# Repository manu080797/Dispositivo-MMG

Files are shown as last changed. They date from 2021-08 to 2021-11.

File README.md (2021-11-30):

# Mecanomiografía: desarrollo de un dispositivo para el monitoreo del límite de fatiga muscular

## Descripción del repositorio

Este es el repositorio del proyecto integrador "Mecanomiografía: desarrollo de un dispositivo para el monitoreo del límite de fatiga muscular" para la carrera de ingeniería mecánica en el <a href="https://www.ib.edu.ar">Instituto Balseiro</a>. En la carpeta <a href="https://github.com/manu080797/Dispositivo-MMG/tree/main/Documentos">Documentos</a> se incluye una <a href="https://github.com/manu080797/Dispositivo-MMG/raw/main/Documentos/Presentación%20final.pptx.zip">presentación de PowerPoint</a> que sirve como introducción al trabajo realizado. Además, se incluye la <a href="https://github.com/manu080797/Dispositivo-MMG/raw/main/Documentos/Mecanomiograf%C3%ADa%20desarrollo%20de%20un%20dispositivo%20para%20el%20monitoreo%20del%20l%C3%ADmite%20de%20fatiga%20muscular.pdf">tesis completa</a> en formato PDF. En la carpeta <a href="https://github.com/manu080797/Dispositivo-MMG/tree/main/Programas">Programas</a> se encuentra el código de los tres programas desarrollados durante el proyecto.  En la carpeta <a href="https://github.com/manu080797/Dispositivo-MMG/tree/main/Electrónica">Electrónica</a> están los archivos de <a href="https://www.kicad.org">KiCAD</a> utilizados para diseñar y construir los circuitos electrónicos del dispositivo. Por último, en la carpeta <a href="https://github.com/manu080797/Dispositivo-MMG/tree/main/Carcasa">Carcasa</a> se incluyen archivos de <a href="https://solidedge.siemens.com/en/solutions/products/complete-product-development-portfolio/whats-new-in-solid-edge-2021/">SolidEdge 2021</a> con el modelo 3D de la carcasa del dispositivo, la cual fue construida con una impresora 3D.

## Resumen
En esta tesis se desarrolló un dispositivo de adquisición de señal para mecanomiografía de bajo costo, replicable y portátil. El mismo consta de un acelerómetro, electrónica de acondicionamiento de señal y una placa de desarrollo en la que se adquieren las señales de dos canales en simultáneo. Estas se procesan digitalmente y son transmitidas de manera inalámbrica a una aplicación multiplataforma de control y comunicación también desarrollada en este trabajo. Esta aplicación permite visualizar las señales en tiempo real y almacenar capturas. Estas se procesan fuera de línea según una metodología también diseñada en este trabajo para determinar qué parámetros de la señal se relacionan con la actividad muscular. Los parámetros se calcularon sobre la señal original, sobre bandas de frecuencia específicas y sobre la distribución espectral de potencia. Por último, se realizaron experimentos para aplicar la metodología propuesta a las señales adquiridas por el dispositivo desarrollado. Se realizaron ejercicios isométricos de extensión de rodilla sobre un brazo de reacción fijo vinculado a una celda de carga. Se midió la señal de mecanomiografía sobre el recto femoral de 5 sujetos en ejercicios a carga máxima, a distintos porcentajes de la carga máxima, y hasta el fallo de la tarea solicitada; y se realizaron pruebas de impacto sobre el músculo para evaluar las propiedades mecánicas del mismo. Se procesaron 145 parámetros, de los cuales se encontraron 12 con alta correlación con la fuerza ejercida (coeficiente de correlación r de Pearson ≥ 0,8). Con las pruebas de impacto se encontró que la frecuencia natural del músculo aumenta con la fuerza. En ejercicios al fallo de la tarea solicitada, se encontró que los 12 parámetros seleccionados mantienen el valor esperado con la correlación hallada, para la carga del ejercicio, durante al menos 10 segundos, y luego presentan desviaciones significativas, pero con sentidos variados entre sujetos. Los parámetros relacionados con la energía de la señal en la banda de 50 a 75 Hz presentaron una correlación superior al resto (r = 0,9) y desviaciones con el tiempo en los ejercicios al fallo consistentes en todos los sujetos y cargas evaluadas.

### Descripción del dispositivo


### Arquitectura del dispositivo


### Arreglo experimental



### Señal cruda en ejercicio al fallo de la tarea solicitada


### Procesamiento de señal
 

### 1) Señal cruda 2) Subbanda de frecuencia 3) Parámetro


## Abstract
A low cost, replicable and portable signal acquisition device for mechanomiography was developed in this thesis. It comprises an accelerometer, its signal conditioning electronics and a development board that acquires the signal in two channels. The signal is digitally processed and wirelessly transmitted to a multi-platform control and communication App, which is also developed in this thesis. This App enables the realtime visualization of the signal and its storage for offline processing, using a methodology designed in this thesis to get correlated features with muscle activity. These features where computed over the original signal, some band filtered components and the power spectrum density. Finally, experiments where conducted to apply the developed methodology to the signal acquired by the device. These experiments consisted of isometric knee extension exercises against a fixed reaction arm linked to a load cell. The mechanomiogram signal was acquired from the rectus femoris muscle of 5 participants at maximum load, at intermediate loads, and to task failure. Additionally, bump tests where conducted to evaluate the muscle mechanical properties. 145 features where processed, of which only 12 showed a high correlation with force (Pearson’s r correlation coefficient ≥ 0,8). Muscle natural frequency was found to increase with higher force production. The 12 selected parameters presented a constant value during the first 10 seconds of a fatiguing exercise, but showed significant deviations from the expected value after this, with varying directions between subjects. From the selected features, those related with the signal energy at the 50-75 Hz band presented both the highest correlation (r = 0,9) and the most consistent deviations sense, in task failure exercises among all subjects and loads.

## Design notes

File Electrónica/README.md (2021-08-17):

# Electrónica

Diagramas esquemáticos y PCB de los circuitos desarrollados. Los mismos se desarrollaron utilizando el software KiCad v5.0.1.

manufactura_pcb

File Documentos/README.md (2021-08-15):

# Documentos

Para una introducción rápida de la tesis ver a presentación de powerpoint. Se debe visualizar con Microsoft PowerPoint en modo presentación, ya que incluye videos y animaciones. En caso de mayores detalles se puede consultar la tesis completa en el archivo PDF.

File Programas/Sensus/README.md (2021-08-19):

# Sensus
Firmware para Sensus (basado en placa de desarrollo Espressif ESP32)

### Flujo de procesamiento de datos


### Diagrama de clases
diagrama_clases_firmware

### Diagrama GRAFCET de la gestión del estado del dispositivo


## Requerimientos:
- Visual Studio Code
- PlatformIO

## Compilación
- Abrir repositorio en Visual Studio Code con la extensión PlatformIO instalada
- Compilar el firmware Sensus usando el comando "PlaformIO: build"
- Conectar la placa de desarrollo ESP32 mediante un cable USB a la computadora
- Modificar el puerto serie/COM en el archivo platformio.ini para que coincida con el puerto asignado al ESP32 por el sistema operativo (ver documentación de PlatformIO)
- Subir el firmware compilado a la placa de desarrollo ESP32 usando el comando "PlaformIO: upload"
- Durante el proceso de subida, PlatformIO espera una conexión exitosa con el dispositivo. Durante esta espera se debe presionar el botón BOOT en la placa de desarrollo para que comienze la carga del firmware en la memoria de la ESP32.

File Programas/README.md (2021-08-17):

# Programas

Programas desarrollados para el dispositivo:

- Sensus: firmware de la placa de desarrollo ESP32. Adquiere la señal analógica en dos canales simultáneamente a 25,6 kHz, realiza un filtrado digital pasa-bajos en dos etapas, remuestrea las señales a 400 Hz y transmite por Bluetooth LE a la aplicación multiplataforma Musculus.

- Musculus: aplicación multiplaforma programada en C# mediante el framework Xamarin. Se comunica con la placa de desarrollo mediante Bluetooth LE. Provee de una interfaz gráfica para controlar el dispositivo de adquisición y visualizar las señales en tiempo real. También permite realizar una captura y compartirla mediante la API de compartir del sistema operativo en que se ejecuta la aplicación. El único código específico de plataforma de la aplicación es el relacionado a la comunicación Bluetooth LE. Este sólo se encuentra implementado para Android, por lo que la aplicación únicamente funciona en dicha plataforma.

- pyMMG: módulo de Python para procesamiento fuera de línea de las capturas tomadas con Musculus. Permite realizar un preprocesamiento para reducir ruido y filtrar ciertas componentes de frecuencia de la señal. Además, realiza una extracción sistemática de parámetros de la señal para luego ser procesados mediante técnicas de análisis de datos. Se incluye un notebook de Jupyter con un ejemplo de uso del módulo.

arquitectura
procesamiento_de_señal

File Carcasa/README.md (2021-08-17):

# Carcasa

Conjunto de SolidEdge 2021 (Student Edition) con modelos 3D de la tapa y base de la carcasa para el dispositivo de adquisición.

carcasa

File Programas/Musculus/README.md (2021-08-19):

# Musculus

## Descripción
Aplicación de control, comunicación y visualización en tiempo real de las señales de mecanomiografía y de fuerza. Se programó en el lenguaje C# en Visual Studio, usando las librerías y plataformas de desarrollo .NET Framework, Xamarin Framework, Xamarin Forms y SkiaSharp. La aplicación se estructura siguiendo el modelo de programación de aplicaciones gráficas modelo-vista-modelo de vista, MVVM por sus siglas en inglés. Se incluye un <a href="https://github.com/manu080797/Dispositivo-MMG/raw/main/Programas/Musculus.apk">archivo APK</a> para instalar la misma directamente en un dispositivo Android sin necesidad de compilar el proyecto en Visual Studio.

aplicacion

## Demo


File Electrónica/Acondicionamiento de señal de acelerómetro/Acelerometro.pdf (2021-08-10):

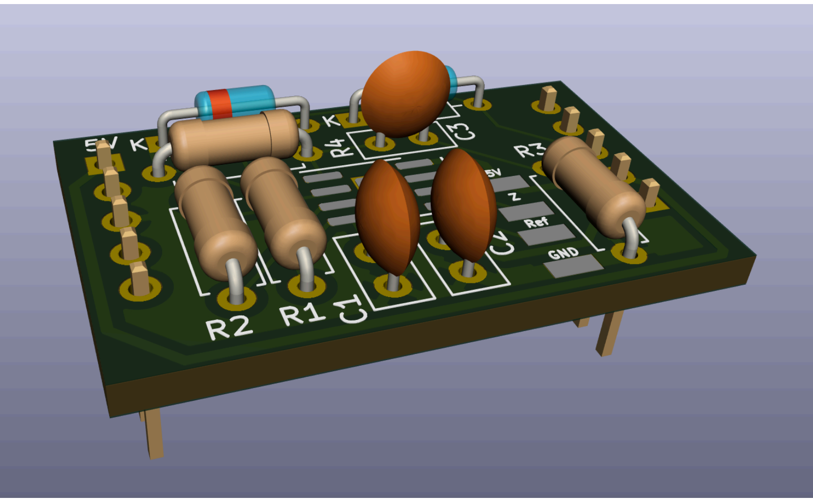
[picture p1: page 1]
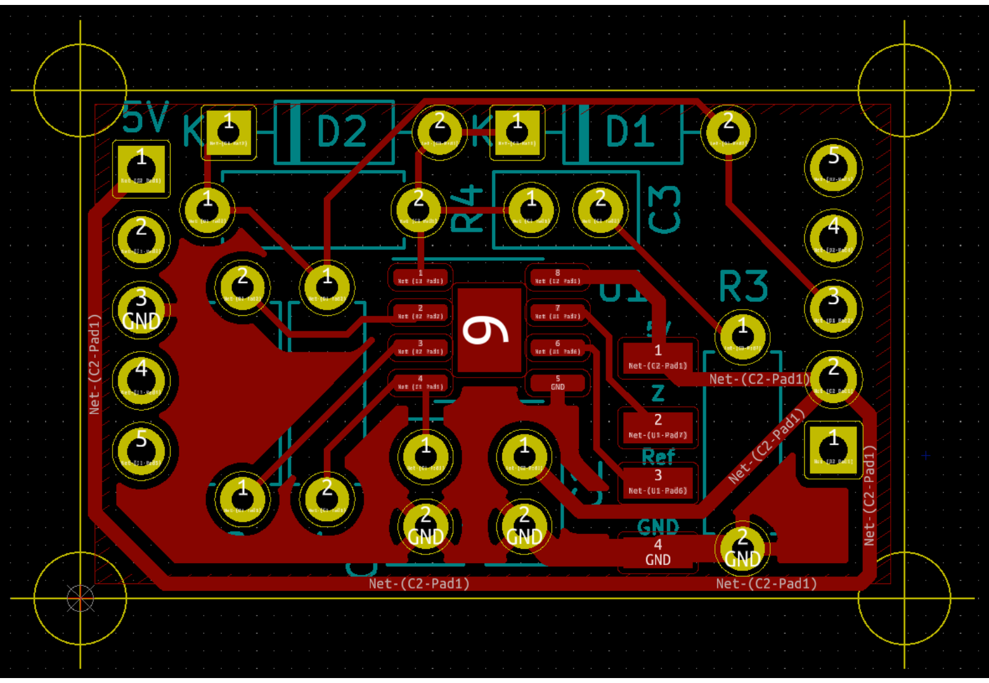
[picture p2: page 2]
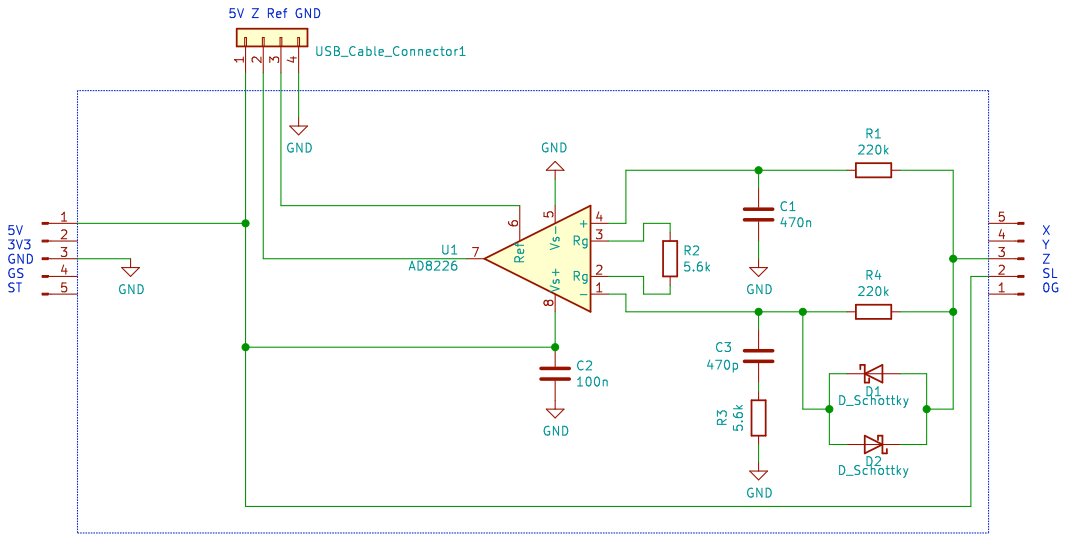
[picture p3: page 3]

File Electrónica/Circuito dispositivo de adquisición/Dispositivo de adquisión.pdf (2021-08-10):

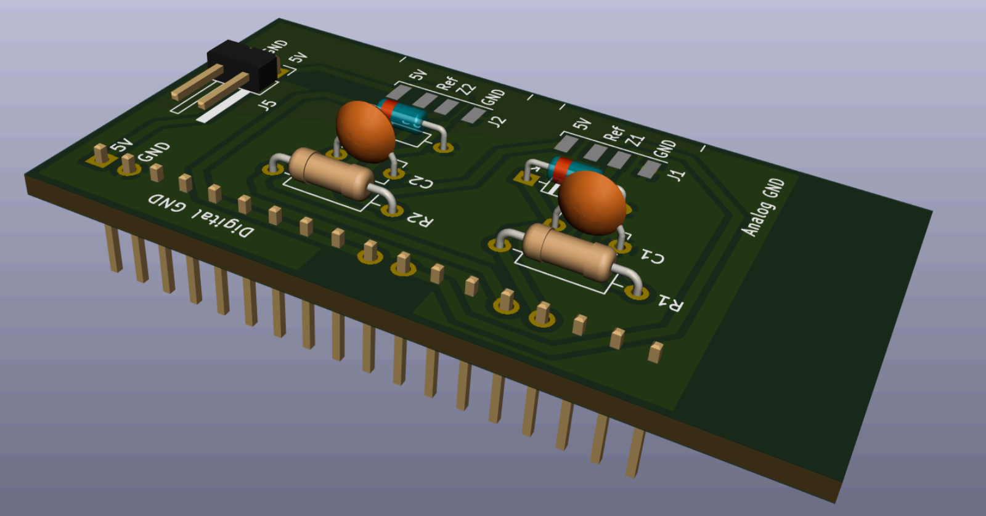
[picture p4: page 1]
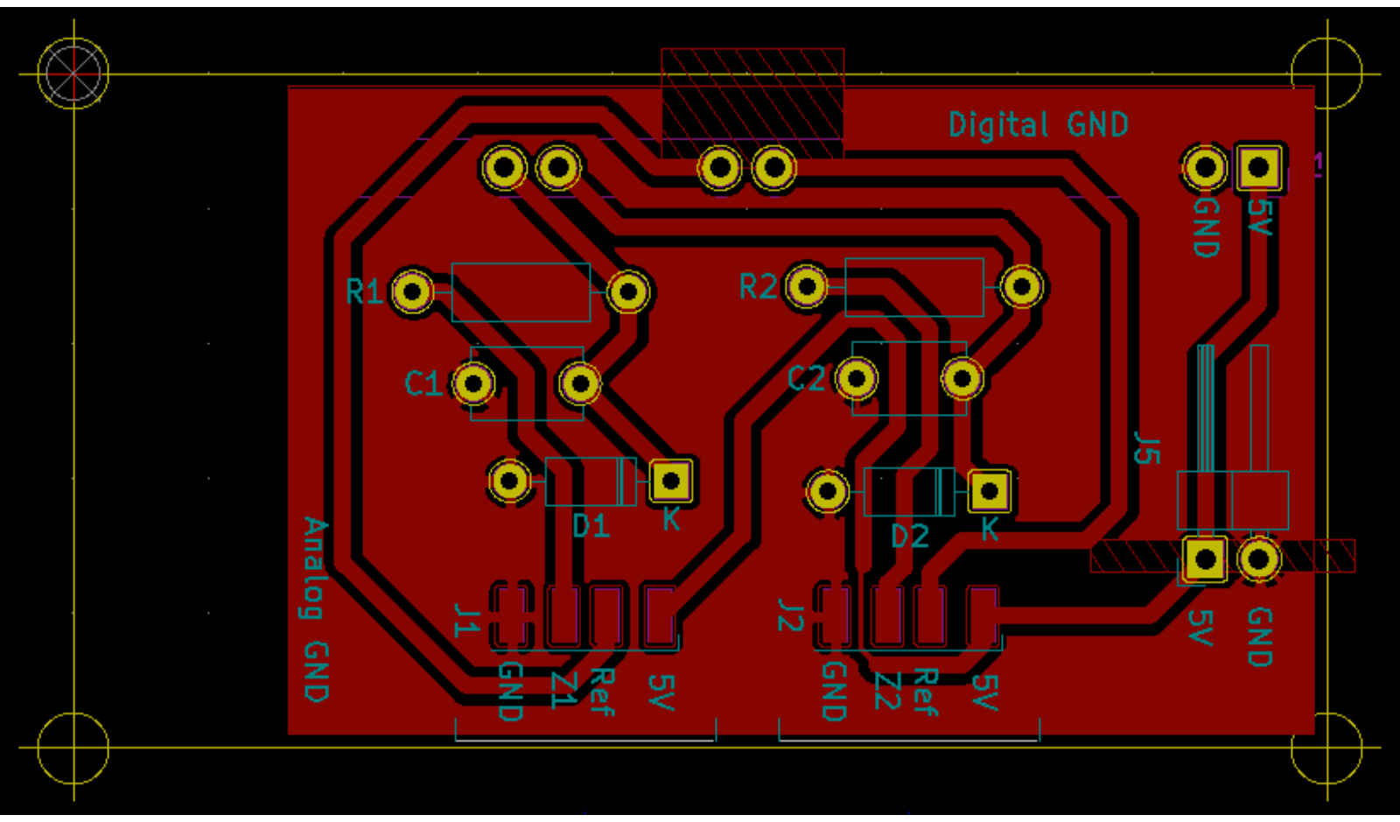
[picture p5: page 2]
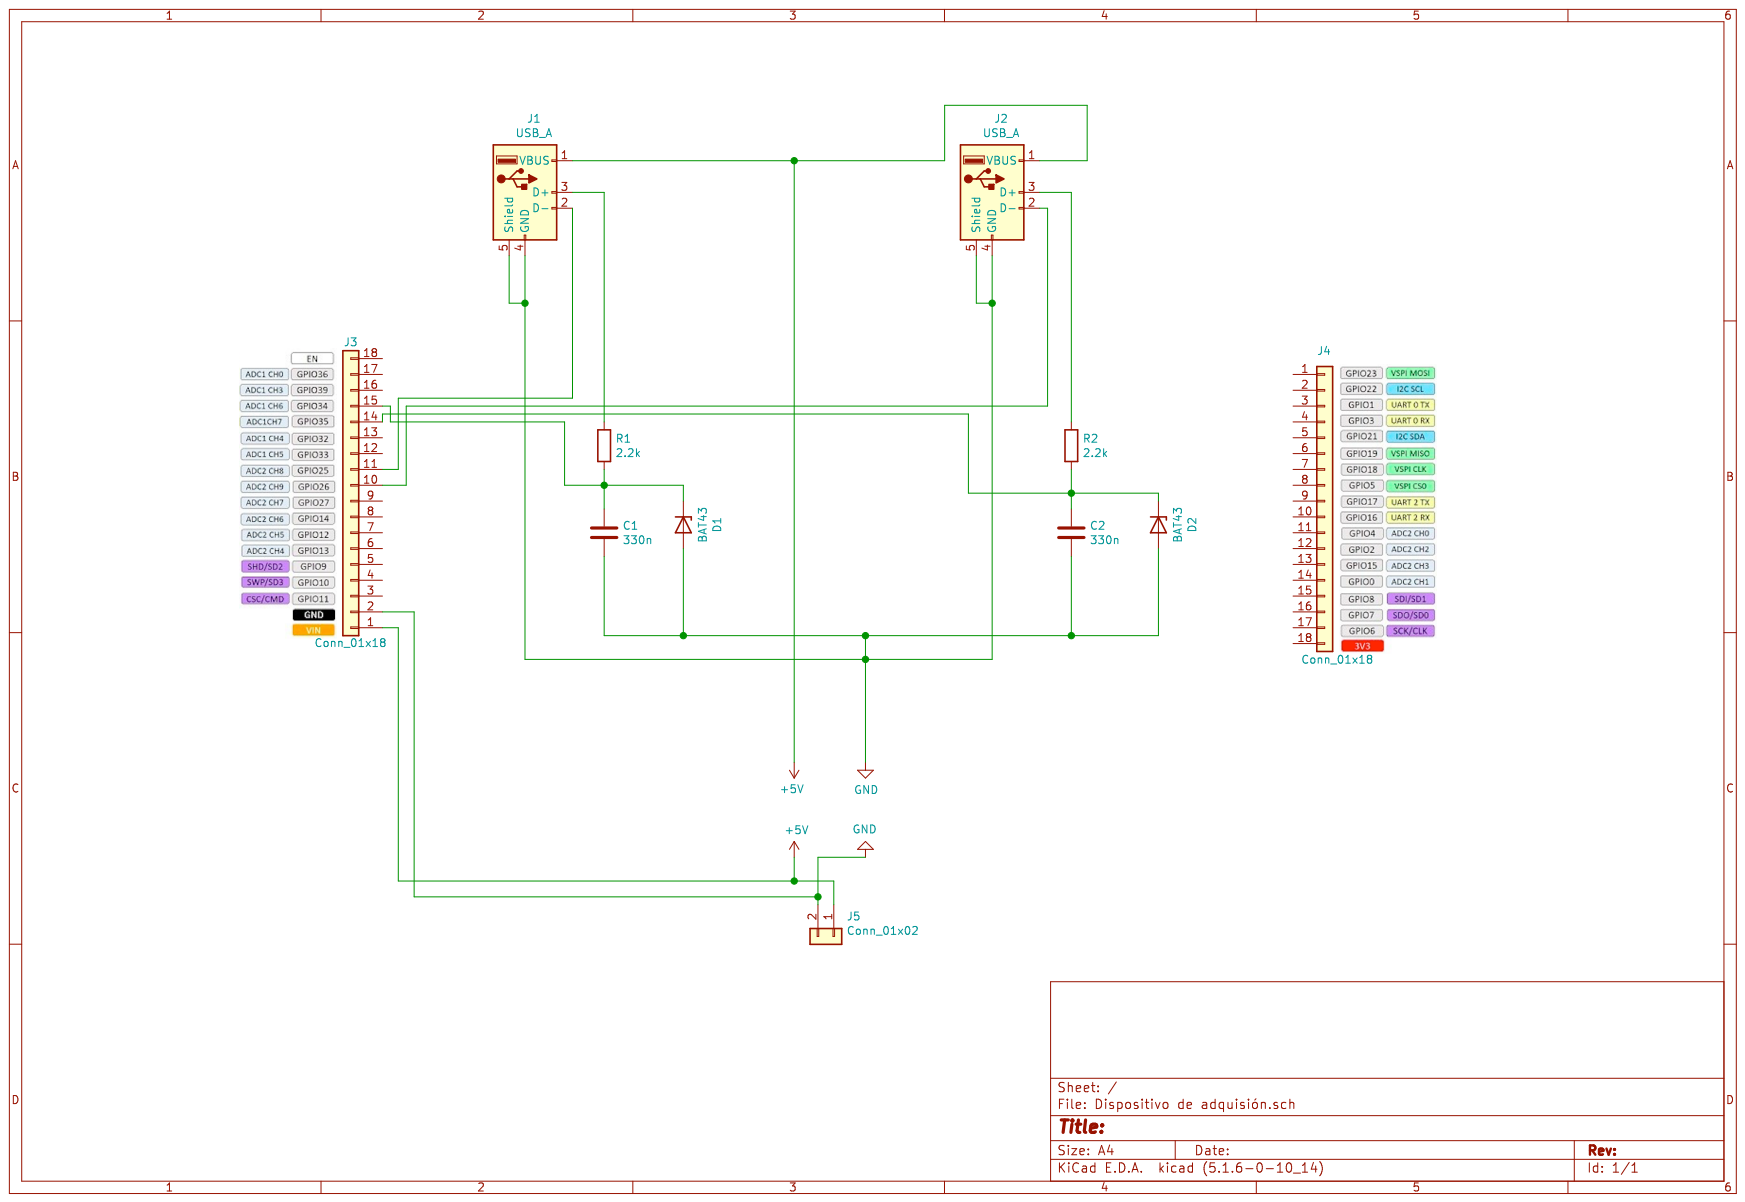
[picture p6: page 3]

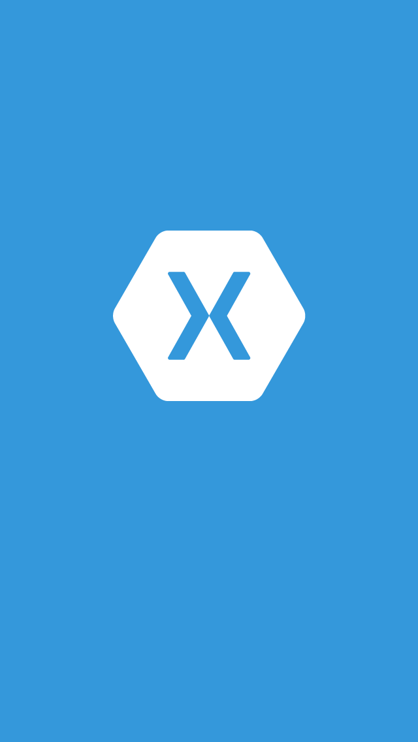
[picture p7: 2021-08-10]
Programas/Musculus/Musculus.iOS/Resources/Default-568h@2x.png

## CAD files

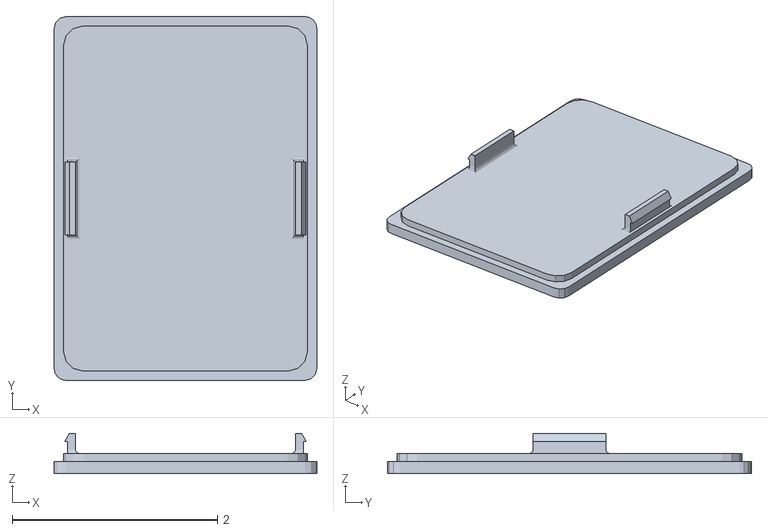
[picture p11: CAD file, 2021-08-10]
Carcasa/Impresión 3D/Tapa.stl
2.56 x 3.54 x 0.394

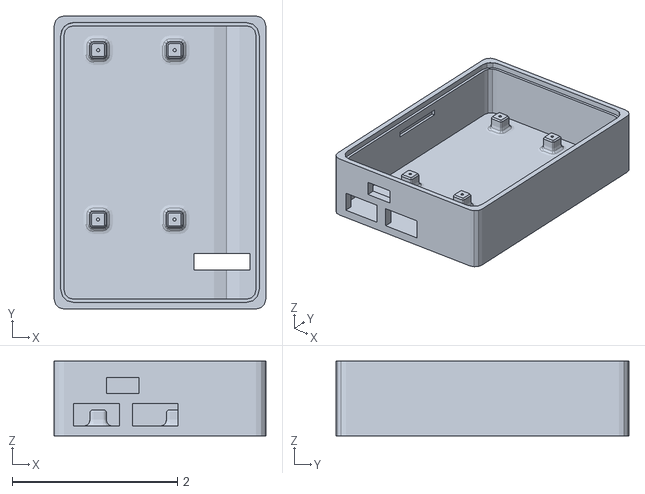
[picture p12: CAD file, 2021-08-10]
Carcasa/Impresión 3D/Base.stl
2.56 x 3.54 x 0.906

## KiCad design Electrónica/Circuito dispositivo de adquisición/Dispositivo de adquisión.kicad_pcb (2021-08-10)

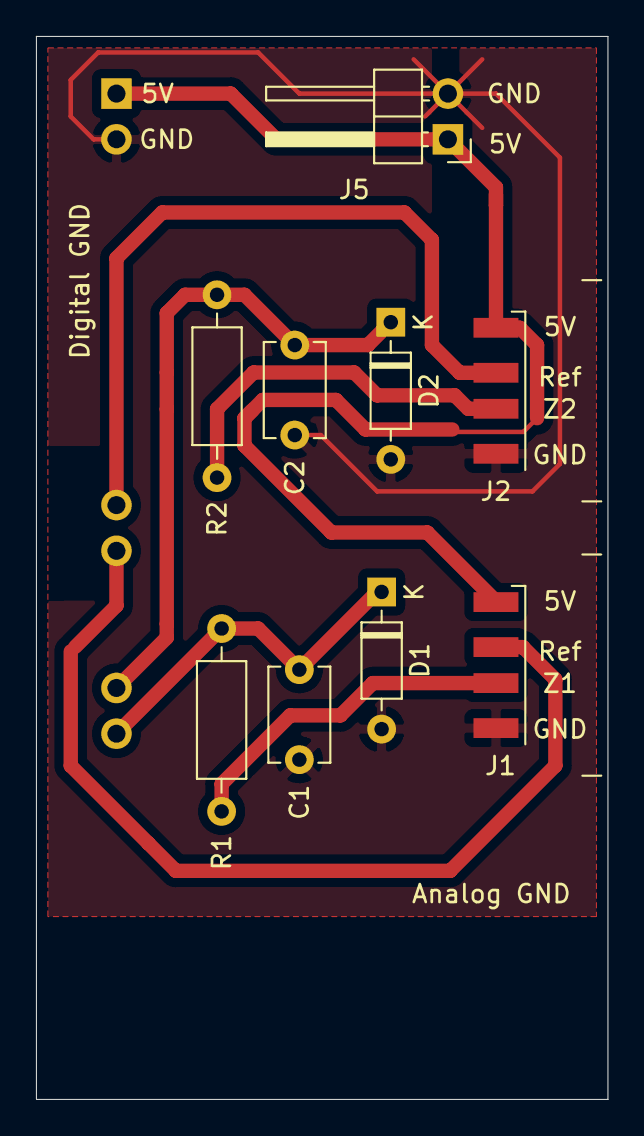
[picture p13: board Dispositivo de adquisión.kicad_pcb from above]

Board: 2 copper layers, 31.7 x 59.1 mm, 10 parts (1 on the bottom side), 8 nets.

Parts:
C1, C2: 330n; C_Disc_D5.1mm_W3.2mm_P5.00mm
D1, D2: BAT43; D_DO-35_SOD27_P7.62mm_Horizontal
J1, J2: USB_A; USB_A_CNCTech_1001-011-01101_Horizontal
J3: Conn_01x18; PinHeader_1x18_P2.54mm_Vertical
J5: Conn_01x02; PinHeader_1x02_P2.54mm_Horizontal
R1, R2: 2.2k; R_Axial_DIN0207_L6.3mm_D2.5mm_P10.16mm_Horizontal

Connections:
+5V: J1.1, J2.1, J3.1, J5.1
GND: C1.2, C2.2, D1.2, D2.2, J1.4, J2.4, J3.2, J5.2
unnamed: C1.1, D1.1, J3.15, R1.2
unnamed: C2.1, D2.1, J3.14, R2.2
unnamed: J1.2, J3.11
unnamed: J1.3, R1.1
unnamed: J2.2, J3.10
unnamed: J2.3, R2.1

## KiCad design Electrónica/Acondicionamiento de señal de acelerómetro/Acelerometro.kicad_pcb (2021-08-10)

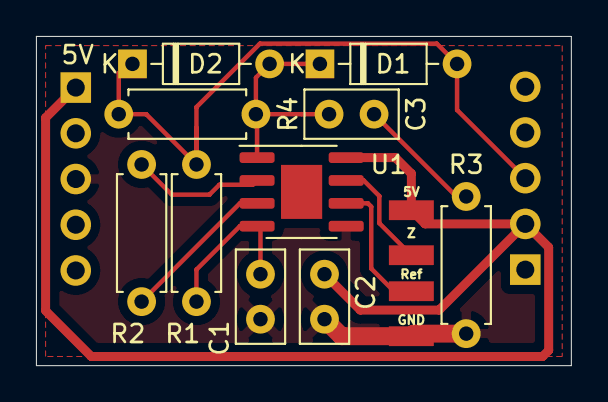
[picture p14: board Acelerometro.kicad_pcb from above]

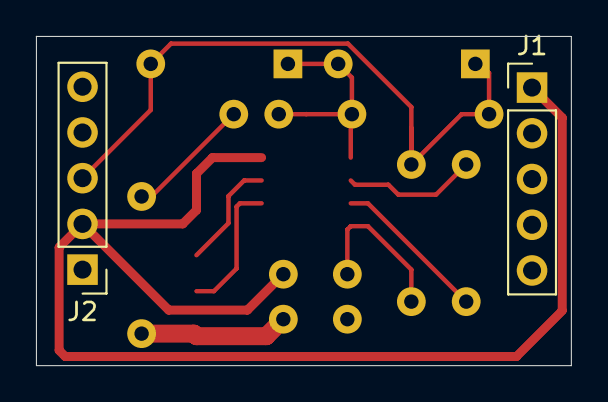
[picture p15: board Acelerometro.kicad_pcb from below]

Board: 2 copper layers, 29.7 x 18.3 mm, 13 parts (2 on the bottom side), 10 nets.

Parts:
C1: 470p; C_Disc_D5.0mm_W2.5mm_P2.50mm
C2: 100n; C_Disc_D5.0mm_W2.5mm_P2.50mm
C3: 470n; C_Disc_D5.0mm_W2.5mm_P2.50mm
D1, D2: D_Schottky; D_DO-35_SOD27_P7.62mm_Horizontal
J1, J2: Conn_01x05_Male; PinHeader_1x05_P2.54mm_Vertical
R1, R4: 220k; R_Axial_DIN0207_L6.3mm_D2.5mm_P7.62mm_Horizontal
R2, R3: 5.6k; R_Axial_DIN0207_L6.3mm_D2.5mm_P7.62mm_Horizontal
U1: AD8226; SOIC-8-1EP_3.9x4.9mm_P1.27mm_EP2.29x3mm
USB_Cable_Connector1: Conn_01x04; USB_A_CNCTech_1001-011-01101_Horizontal

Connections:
GND: C1.2, C2.2, J1.3, R3.2, U1.5, USB_Cable_Connector1.4
unnamed: C1.1, R1.2, U1.4
unnamed: C2.1, J1.1, J2.2, U1.8, USB_Cable_Connector1.1
unnamed: C3.1, D1.1, D2.2, R4.2, U1.1
unnamed: C3.2, R3.1
unnamed: D1.2, D2.1, J2.3, R1.1, R4.1
unnamed: R2.1, U1.3
unnamed: R2.2, U1.2
unnamed: U1.6, USB_Cable_Connector1.3
unnamed: U1.7, USB_Cable_Connector1.2

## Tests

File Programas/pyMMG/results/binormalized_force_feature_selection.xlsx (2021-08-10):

 | Feature | lambda | r | tau | tau target | % H0 same target rejected | % H0 same subject rejected
0 | MMG MeanOfAmplitude | 0.5709321139 | 0.8153057212 | 0.6082235812 | 0.6274069037 | 0 | 0.2222222222
1 | Banda ada MeanOfAmplitude | 0.4788991954 | 0.9049367566 | 0.7260688022 | 0.7469664029 | 0 | 0.2222222222
2 | Banda ada Variance | 0.2090857679 | 0.8850949915 | 0.7112594916 | 0.7318387355 | 0 | 0.2222222222
3 | Banda ada InstantaneousAmplitude | 0.478669995 | 0.9050481143 | 0.7263317627 | 0.7472588801 | 0 | 0.2222222222
4 | Banda add MeanOfAmplitude | 0.5948586085 | 0.8004289495 | 0.6057442944 | 0.6336274593 | 0 | 0.1111111111
5 | MMG NumberOfTurns | 2.174413337 | 0.8415933734 | 0.6422354479 | 0.6825406927 | 0 | 0.3333333333
6 | Banda ada MMGScore | 0.7581417084 | 0.8759487338 | 0.6864880437 | 0.7065113957 | 0 | 0.2222222222
7 | MMG Frequency Variance (Avg) | 1.171404444 | 0.8944489816 | 0.7113774997 | 0.7448268289 | 0 | 0.7777777778
8 | MMG Frequency Entropy (Avg) | 7.93169115 | 0.8655048922 | 0.6641756775 | 0.7027363033 | 0 | 0.3333333333
9 | MMG Frequency InterquantileRange50 (Avg) | 1.068116419 | 0.8712754464 | 0.6790264272 | 0.7147366315 | 0 | 0.4444444444
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

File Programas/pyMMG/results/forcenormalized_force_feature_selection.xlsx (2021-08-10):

 | Feature | lambda (avg) | r (min) | tau (min) | tau target (min) | % H0 same target rejected
0 | Banda ada MeanOfAmplitude | 0.5264265247 | 0.9231250257 | 0.7208199344 | 0.7486081753 | 0
1 | Banda ada Variance | 0.2468268166 | 0.8901223951 | 0.6921787754 | 0.7181670375 | 0
2 | Banda ada InstantaneousAmplitude | 0.5260651758 | 0.9237604676 | 0.7212142773 | 0.7490188586 | 0
3 | MMG NumberOfTurns | 2.336693094 | 0.8460028784 | 0.6528574656 | 0.6910013396 | 0
4 | Banda ada MMGScore | 0.8994897156 | 0.9172020107 | 0.7370309665 | 0.769371131 | 0
5 | MMG Frequency Mean (Avg) | 2.544238883 | 0.8043307784 | 0.6060028273 | 0.6297758679 | 0
6 | MMG Frequency Variance (Avg) | 1.168232186 | 0.8510521746 | 0.6618382626 | 0.6945168669 | 0
7 | MMG Frequency Entropy (Avg) | 8.702489342 | 0.8840998604 | 0.6866097623 | 0.7049222191 | 0
8 | MMG Frequency InterquantileRange50 (Avg) | 0.9964637341 | 0.8111848009 | 0.6113844843 | 0.6466301476 | 0
9 | MMG Frequency Quantile75 (Avg) | 2.081670504 | 0.8292170925 | 0.6319696897 | 0.6512035271 | 0
